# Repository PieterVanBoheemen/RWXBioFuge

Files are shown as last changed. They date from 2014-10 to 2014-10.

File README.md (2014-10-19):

RWXBioFuge
==========

Centrifugation is a powerful method for isolation of compounds such as DNA, proteins, oil or membrane vesicles from a complex mixture. The RWXBioFuge was designed to bring this powerful tool into the hands of labtechnicans, scientists, hackers, makers, diybio-ers and those who cannot afford to procure A-label equipment in low-resource settings. 

It may also be used as an educational project to teach some fundamental principles of physics, chemistry, biology and electronics hands-on. Apart from an assembly guide, this documentation also includes [7 instructions for demonstration experiments and science classes][6].

For assembly workshops or any questions, remarks or suggestions please contact pietervanboheemen@gmail.com

This repository contains the code, source files and instructions for operating the RWXBioFuge Open Source microcentrifuge.

- [ArduinoCode][1]: source code for the Arduino Ethernet
- [Rotor][2]: OpenSCAD source code for the rotor, preview at [YouMagine][5]
- [Device][3]: Bill of Materials, 3D model, 2D CAD files and Fritzing wiring
- [Docs][4]: assembly and tutorial documents

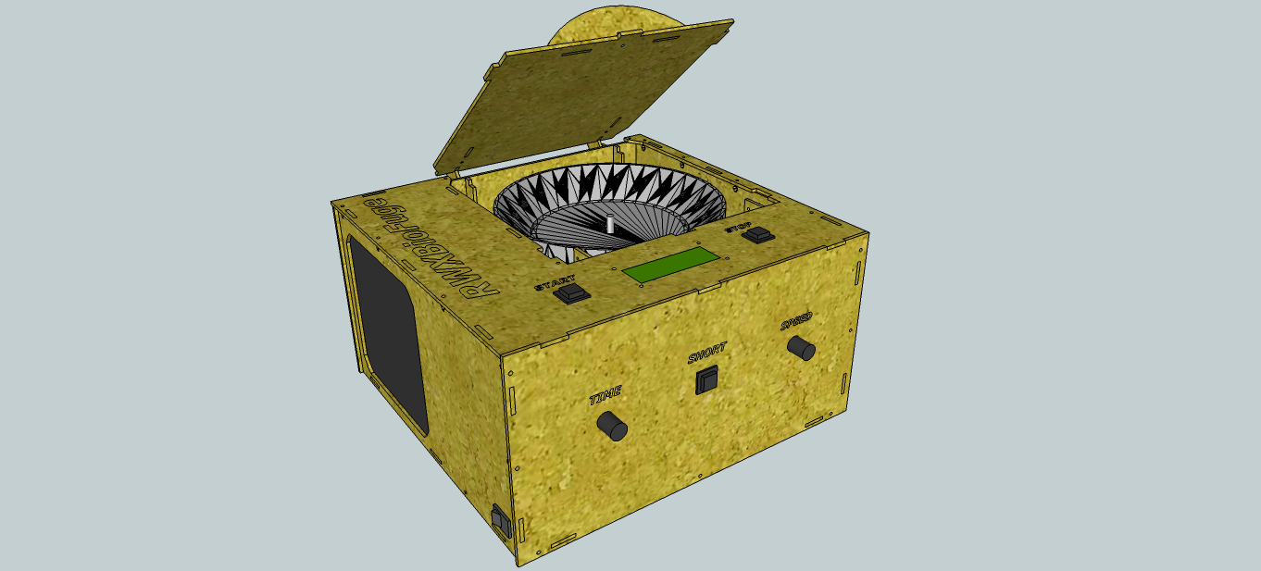
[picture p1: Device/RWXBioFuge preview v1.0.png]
Render

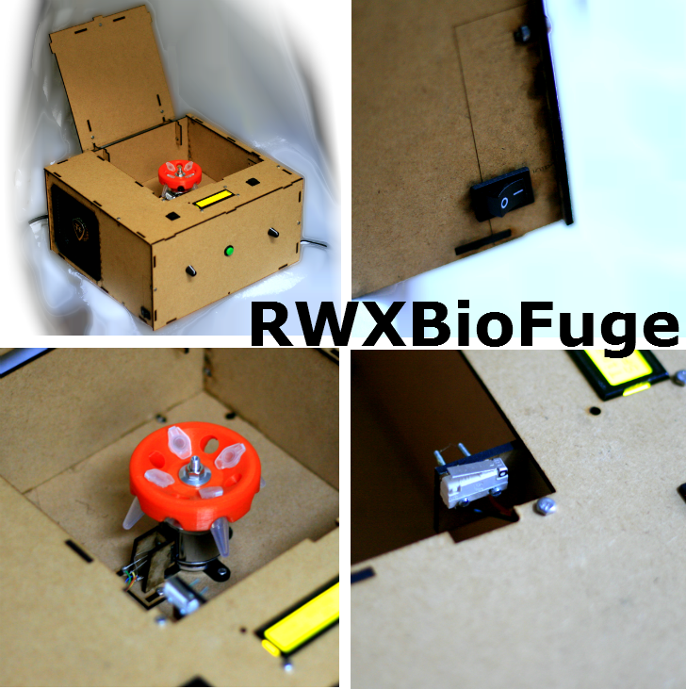
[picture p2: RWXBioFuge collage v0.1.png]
Pictures

Beneden Leeuwen

The V0.1 machine is used in the [Waag Society's Open Wetlab][10] and future improvements will be made during the [Open Wetlab open evenings][11].

> **WARNING**: Fast spinning rotors are dangerous! Make sure you read the [safety instructions][7] before use.

> **LICENSE**: All work in this project is licensed under the [Creative Commons Attribution-ShareAlike 4.0 International License][8]. In other words: you are free to use everything in this repository as long as you attribute Pieter van Boheemen and share derivative work under the same conditions.

###Release notes and features of V1.0
The V1.0 release of the RWXBioFuge contains the following features:
- Completely Open Source and designed in freely available software, such as Arduino IDE, Sketchup, OpenSCAD, InkScape and Fritzing 
- Constructed out of solely off-the-shelf or digitally fabricated parts
- High speed centrifuge > 10,000 RPM, depending on your own settings and confidence
- Configurable speed in percentages of full power
- Configurable time in convenient steps, including infinite
- Separate Start and Stop buttons
- Current RPM, Gforce and remaining time is displayed during operation
- A button for Short immediate operation
- Open lid detector
- Web interface to set, start and stop the machine, including status during operation

###Release notes of V0.1
V0.1 is the first development release of RWXBioFuge. It is still in experimental phase with plenty of bugs. All V0.1 source files will be replaced when V1.0 is ready.

###To Do
The following upgrades are planned for the next version:
- Step by step graphical assembly guide in Instructables style
- Optimization of Power Supply, ESC and motor setup to save costs
- Reduced size of the casing by better placement of components
- Single rotary encoder interface to save costs
- Magnetic lid lock to increase safety
- Accelerometer for the detection of unbalanced rotor through vibrations to increase safety
- Transparent window in lid
- Numbered tube holes in rotor
- Different types of rotors, for various number and sizes of tubes and Hct
- Improved graphical Web User Interface 

Credits: This project has been greatly inspired by the work, advise and help of:

    DIYBio Groningen for printing the first rotor at Beneden-Leeuwen Mini Maker Faire
	Cathal Garvey - Dremelfuge
    Karlin Yeh - OpenFuge
    Drevious - Microfuge 8 Place Rotor
    Hackteria - Hacked Hard Disk centrifuge

[1]:https://github.com/PieterVanBoheemen/RWXBioFuge/blob/master/ArduinoCode/
[2]:https://github.com/PieterVanBoheemen/RWXBioFuge/blob/master/Rotor/
[3]:https://github.com/PieterVanBoheemen/RWXBioFuge/blob/master/Device/
[4]:https://github.com/PieterVanBoheemen/RWXBioFuge/blob/master/Docs/
[5]:https://www.youmagine.com/designs/microcentrifuge-20-place-rotor
[6]:https://github.com/PieterVanBoheemen/RWXBioFuge/blob/master/Docs/Tutorials/
[7]:https://github.com/PieterVanBoheemen/RWXBioFuge/blob/master/Docs/Usage/
[8]:http://creativecommons.org/licenses/by-sa/4.0/
[9]:http://www.diybiogroningen.org/mini-mini-maker-faire-in-beneden-leeuwen/
[10]:http://waag.org/en/lab/open-wetlab
[11]:http://www.meetup.com/Dutch-DIY-Bio/

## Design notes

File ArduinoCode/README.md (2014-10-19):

RWXBioFuge Arduino Code
=======================

Input:
- Time rotary encoder
- RPM rotary encoder
- Start button
- Short run button
- Lid detector
- Infrared RPM sensor
- Ethernet

Output:
- Pulses for Electronic Speed Controller
- Serial USB
- Ethernet
- I2C 16x2 LCD display

Dependencies:
- Webduino https://github.com/sirleech/Webduino
- AdaEncoder https://code.google.com/p/adaencoder/
- ooPinChangeInt https://code.google.com/p/oopinchangeint/
- LiquidCrystal_I2 http://hmario.home.xs4all.nl/arduino/LiquidCrystal_I2C/

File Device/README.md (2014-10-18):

Device
======

The RWXBioFuge consists of solely of-the-shelf parts and laser cut wood that has been designed in Sketchup. Using these source files and the [Assembly Guide][1], you can build your own.

In this folder you will find:

- The Bill of Materials (BoM)
- 3D SketchUp design file
- 2D SVG files of each part
- Fritzing wiring of Breadboard or Shield

[1]: https://github.com/PieterVanBoheemen/RWXBioFuge/blob/master/Docs/Assembly/

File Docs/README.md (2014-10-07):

RWXBioFuge documentation
=======================

This folder contains the documentation of the RWXBioFuge project, including an assembly guide, usage instructions and tutorial experiments. 

----------

#### Assembly Guide
Information on how to assemble the RWXBioFuge. [Read Assembly Guide][1]
#### Tutorial Experiments
Fun experiments to start exploring the usage of the RWXBioFuge. [Read Tutorial Experiments][2]
#### Usage Instructions
Basic instructions on how to use the RWXBioFuge. [Read Usage Instructions][3]

[1]:https://github.com/PieterVanBoheemen/RWXBioFuge/blob/master/Docs/Assembly/
[2]:https://github.com/PieterVanBoheemen/RWXBioFuge/blob/master/Docs/Tutorials/
[3]:https://github.com/PieterVanBoheemen/RWXBioFuge/blob/master/Docs/Usage/

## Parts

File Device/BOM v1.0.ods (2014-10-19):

The links offered in this BoM are mere suggestions. Have a look on eBay or Alibaba to find cheaper alternatives
Description | Amount | URL | Remarks
Push button | 3 | http://nl.farnell.com/apem/1415nc-black/switch-spdt-black/dp/1082275?Ntt=1082275 | APEM - 1415NC BLACK - SWITCH, SPDT, BLACK
Lid lever switch | 1 | http://nl.farnell.com/itw-switches/19n403l18/microswitch-v4-lever/dp/624676?Ntt=624676 | ITW SWITCHES - 19N403L18 - MICROSWITCH, V4, LEVER
IR RPM sensor | 1 | http://nl.farnell.com/fairchild-semiconductor/qrd1114/opto-switch-reflective/dp/1467858?Ntt=1467858 | FAIRCHILD SEMICONDUCTOR - QRD1114 - OPTO SWITCH, REFLECTIVE
16x2 LCD display with I2C module | 1 | https://iprototype.nl/products/components/led-lcd/lcd16x2-I2C-BL | These displays are also commonly found on eBay: http://www.ebay.com/itm/1602-LCD-16X2-Character-Display-IIC-I2C-TWI-SPI-I2C-Serial-Interface-Board-/371158866343?pt=LH_DefaultDomain_0
Rotor | 1 | https://www.youmagine.com/designs/microcentrifuge-20-place-rotor | Print it yourself, via Shapeways or 3Dhubs
Power Supply | 1 | http://www.thermaltake.com/products-model.aspx?id=C_00001830 | ThermalTake SMART M850W
Electronic Speed Controller | 1 | http://www.hobbyking.com/hobbyking/store/uh_viewItem.asp?idProduct=33371 | Hobbyking SS Heli Series 50-65A ESC
Brushless motor | 1 | http://www.hobbyking.com/hobbyking/store/uh_viewItem.asp?idProduct=39962 | Turnigy Aerodrive SK3 - 4240-740kv Brushless Outrunner Motor
Power switch | 1 | https://iprototype.nl/products/components/buttons-switches/rocker-switch-large | RLEIL ROCKER SWITCH
Arduino Ethernet |  |  | Buy it at your favorite Arduino dealer
Lasercut out of 3mm MDF |  |  | Cut it yourself, or via Ponoko / Formulor
2.2kOhm | 4 | http://nl.farnell.com/multicomp/mcf-0-25w-2k2/resistor-carbon-film-2k2-0-25w/dp/9339302?Ntt=9339302 | MULTICOMP - MCF 0.25W 2K2 - RESISTOR, CARBON FILM, 2K2, 0.25W, 5%
220Ohm | 1 | http://nl.farnell.com/multicomp/mcf-0-25w-220r/resistor-carbon-film-220r-0-25w/dp/9339299?Ntt=9339299 | MULTICOMP - MCF 0.25W 220R - RESISTOR, CARBON FILM, 220R, 0.25W, 5%
6.8kOhm | 1 | http://nl.farnell.com/multicomp/mcf-0-25w-6k8/resistor-carbon-film-6k8-0-25w/dp/9339663?Ntt=9339663 | MULTICOMP - MCF 0.25W 6K8 - RESISTOR, CARBON FILM, 6K8, 0.25W, 5%
Rotary encoder | 2 | https://www.sparkfun.com/products/9117 | ALPHA 318-ENC130175F-12PS
Knob | 2 | http://nl.farnell.com/multicomp/cr-r4-7/knob-soft-touch-d-shaft-black/dp/1440012?Ntt=1440012 | MULTICOMP - CR-R4-7 - KNOB, SOFT TOUCH, D SHAFT, BLACK
3.5 mm connectors | 1 | http://www.hobbyking.com/hobbyking/store/__20228__Individual_HXT_3_5mm_connector_for_motor_ESC_12pc_.html | Individual HXT 3.5mm connector for motor/ESC
Protoshield | 1 | http://nl.farnell.com/arduino/a000082/prototype-shield-for-arduino-board/dp/2075379?Ntt=2075379 | ARDUINO - A000082 - PROTOTYPE SHIELD, FOR ARDUINO BOARD
Molex extension | 1 | https://www.sparkfun.com/products/11298 | 4 Pin Molex Connector – Pigtail
Stackable headers | 1 | http://www.antratek.nl/arduino-stackable-header-kit | Arduino Stackable Header Kit
M3 10 nuts and bolts | 1 | http://www.bevestigingsmateriaal.nl//index.php?productGroupId=61&productId=65210093303005 | Buy it at your local Do-It-Yourself hardware store
Generic stuff
Solder | 1
Tie wrap | 1
Wires | 20

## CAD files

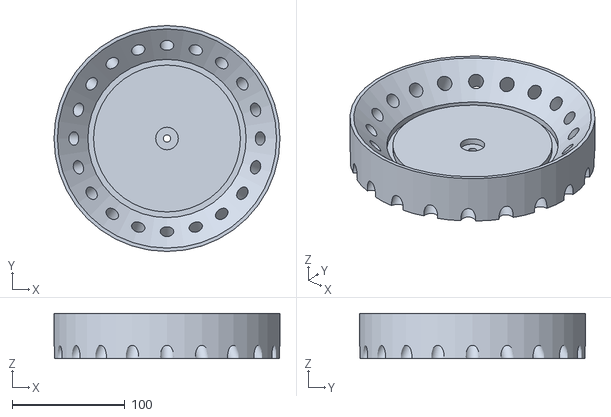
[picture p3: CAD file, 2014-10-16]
Rotor/rotor v0.1.stl
200.0 x 200.0 x 40.0

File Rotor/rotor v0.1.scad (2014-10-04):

$fn=40; // resolution of the arcs

scale([10,10,10]) { // cm to mm scaling

difference () { // substract tube holders from outer ring

difference () { // substract inner groove

	difference() { // substract cone from main disk

		translate([0,0,-0.4])
		cylinder (h = 4, r=12); // main disk

		translate([0,0,1]) // raise cone from bottom
		cylinder (h = 2.7, r1 = 8, r2 = 10.8, center = false); // cone

		translate([0,0,-0.6])
		cylinder (h = 1.6, r=0.635); // axis

		translate([0,0,0.5]) // groove around axis
		cylinder (h = 0.5, r=1);

	}

	// groove under tube holders
	translate([0,0,0.5])
	difference() { // ring
		cylinder (h = 0.5, r = 8);
		cylinder (h = 0.5, r = 7.5);
	}

}

//tube holding cylinders
translate([-11.5,0,-1]) rotate([0,35,0]) cylinder(h=8, r=1.2);
translate([11.5,0,-1]) rotate([0,-35,0]) cylinder(h=8, r=1.2);

translate([0,-11.5,-1]) rotate([0,35,90]) cylinder(h=8, r=1.2);
translate([0,11.5,-1]) rotate([0,-35,90]) cylinder(h=8, r=1.2);

translate([-11.5 * cos(22.5), -11.5 * sin(22.5),-1]) rotate ([0,35,22.5]) cylinder(h=8, r=1.2);
translate([-11.5 * cos(45),-11.5 * sin(45),-1]) rotate ([0,35,45]) cylinder(h=8, r=1.2);
translate([-11.5 * cos(67.5),-11.5 * sin(67.5),-1]) rotate ([0,35,67.5]) cylinder(h=8, r=1.2);

translate([-11.5 * cos(22.5), 11.5 * sin(22.5),-1]) rotate([0,35,-22.5]) cylinder(h=8, r=1.2);
translate([-11.5 * cos(45), 11.5 * sin(45),-1]) rotate([0,35,-45]) cylinder(h=8, r=1.2);
translate([-11.5 * cos(67.5), 11.5 * sin(67.5),-1]) rotate([0,35,-67.5]) cylinder(h=8, r=1.2);

translate([11.5 * cos(22.5), -11.5 * sin(22.5),-1]) rotate([0,-35,-22.5]) cylinder(h=8, r=1.2);
translate([11.5 * cos(45), -11.5 * sin(45),-1]) rotate([0,-35,-45]) cylinder(h=8, r=1.2);
translate([11.5 * cos(67.5), -11.5 * sin(67.5),-1]) rotate([0,-35,-67.5]) cylinder(h=8, r=1.2);

translate([11.5 * cos(22.5), 11.5 * sin(22.5),-1]) rotate([0,-35,22.5]) cylinder(h=8, r=1.2);
translate([11.5 * cos(45), 11.5 * sin(45),-1]) rotate([0,-35,45]) cylinder(h=8, r=1.2);
translate([11.5 * cos(67.5), 11.5 * sin(67.5),-1]) rotate([0,-35,67.5]) cylinder(h=8, r=1.2);
}

}

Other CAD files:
Device/RWXBioFuge v1.0.skp

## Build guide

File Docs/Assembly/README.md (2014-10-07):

Assembly Guide
==============

Hi fellow DIY Centrifugator,

Welcome to the RWXBioFuge assembly guide! By following these step by step instructions you will have your RWXBioFuge spinning within 2 hours. Finally the force of centrifugation on your DIY lab bench at your disposal.

Whenever you feel like something is unclear, use the commenting section here on GitHub to post your remarks.

The assembly guide consists of four steps:

- [00 Getting Started][0]
- [01 Casing][1]
- [02 Wiring][2]
- [03 Programming][3]
- [04 Final][4]

[0]: https://github.com/PieterVanBoheemen/RWXBioFuge/blob/master/Docs/Assembly/00-Getting-Started.md
[1]: https://github.com/PieterVanBoheemen/RWXBioFuge/blob/master/Docs/Assembly/01-Casing.md
[2]: https://github.com/PieterVanBoheemen/RWXBioFuge/blob/master/Docs/Assembly/02-Wiring.md
[3]: https://github.com/PieterVanBoheemen/RWXBioFuge/blob/master/Docs/Assembly/03-Programming.md
[4]: https://github.com/PieterVanBoheemen/RWXBioFuge/blob/master/Docs/Assembly/04-Final.md

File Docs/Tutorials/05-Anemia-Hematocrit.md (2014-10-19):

05 Anemia diagnosis and hematocrit measurement
==============================================

> **WARNING**: Blood may carry diseases such as HIV and Hepatitis B. Wear protective gloves when handling other peoples blood and clean everything thoroughly. DIY experiments should never be interpreted as a medical diagnosis, go see a doctor instead.

Hematocrit values are measured to determine whether blood has a sufficient number of erythrocytes. These are necessary to transfer oxygen. However, if the concentration is too high, the blood's viscosity becomes a problem.

The blood of consists of plasma, red blood cells and white blood cells. When a sample is centrifuged, the red cells sink to the bottom. The plasma will be on top and a thin layer of white cells can be found on top of the red cells pellet. The volume ratio between red cells and the total volume is the Hct value.

Normal Hct values are around 47 percent for men, and 42 percent for women. Anemia occurs when the Hct value is below 40 for men, and below 37 for women.

### Materials
- Ethanol (70%)
- Soap and water
- Gloves
- Sterile lancets
- Cotton ball
- Hematocrit tubes (for which you need a hematocrit head), or small centrifuge tubes preferably graded
- Trash container

### Procedure
- Wash your hands with soap and water
- Clean a finger you don't use that much, such as ring finger, with 70% ethanol
- Pierce the fingertip with a quick prick to the side
- The first liquid is hardly any blood, so wipe it off with the clean and dry cotton ball
- By squeezing your fingertip blood will drip into the hematocrit or centrifuge tube
- Balance a second tube with the same weight and place on opposite sides of the centrifuge
- Spin at full speed for 5 minutes
- Determine the percentage of red blood cells

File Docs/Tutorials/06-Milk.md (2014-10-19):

06 Break down whole milk into cream and skim milk
=================================================

Whole milk consist for about 4% of fat. Centrifuges can be used to separate the cream from the skim milk.

### Materials
- 2 mL centrifuge tubes (for bigger volumes you need a different rotor)
- Whole milk
- Transfer pipettes
- Stove
- Thermometer

### Procedure
- Warm up the whole milk to about 40 degrees Celcius
- Transfer the whole milk into centrifuge tubes. Make sure they're balanced.
- Spin at maximum speed for 5 minutes
- Observe the separation
- Try to pipette the skim milk into fresh tubes

### Additional steps
You may continue to analyse the resulting cream and skim milk with a density meter or even a microscope.

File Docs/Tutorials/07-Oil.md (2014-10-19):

07 Oil and water separation
===========================

In this experiment we will investigate the influence of detergents on the ability of the centrifuge to seperate water and oil.

### Materials
- Oil, such as olive oil, sunflower oil or palm oil
- Water from the tap
- Centrifuge tubes
- Detergent, such as hand soap or dishwashing soap 

### Procedure
- Prepare a dilution series of oil in water
- Add different concentrations of detergent to the mixture
- Make sure the tubes are balanced
- Spin in the centrifuge at max speed for 5 minutes
- Observe the separation profiles

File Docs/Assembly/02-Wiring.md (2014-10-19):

02 Wiring
=========

The second step is to wire all the components. Take a close look at the [Fritzing arduino shield wiring schematic][1] before connecting all the components.

1. Prepare molex connector
2. Connect brushless motor to molex connector and ATX power supply
3. Connect power switch to ATX power supply
4. Connect Electronic Speed Controller to brushless motor
5. Wire everything to the arduino shield, overlayed with the "RWXBioFuge Shield port indicator"
  1. Connect Electronic Speed Controller
  2. Connect Infra-red RPM sensor 
  3. Connect Lid lever switch
  4. Connect Electromagnet
  5. Connect the Start push button
  6. Connect the Stop push button
  7. Connect the Short push button
  6. Connect the Time rotary encoder
  7. Connect the Speed rotary encoder
  7. Connect I2C LCD
  8. Connect power supply 

> **Tip:** Use tie wraps to bundle the wires.

Continue to the following step [03 Programming][0].

[0]:https://github.com/PieterVanBoheemen/RWXBioFuge/blob/master/Docs/Assembly/03-Programming.md
[1]:https://github.com/PieterVanBoheemen/RWXBioFuge/blob/master/Device/Shield%20v1.0.fzz

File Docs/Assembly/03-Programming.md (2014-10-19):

03 Programming
==============

The third step is to preparing the Arduino Ethernet.

1. Download the latest RWXBioFuge source code and libraries from [Github][1].
2. Connect the USB to serial programming board to the Arduino Ethernet and put the USB cable in your computer.
3. Load the RWXBioFuge source code in the Arduino IDE.
4. Click on Upload to compile and transfer the code to the Arduino Ethernet.
5. Disconnect the USB to serial programming board from the Arduino Ethernet.
6. Assemble the RWXBioFuge proto shield on to the Arduino Ethernet.
7. Power up the RWXBioFuge and check whether the LCD starts by showing "RWXBioFuge" and continues to the settings menu.

Almost done, just one more step left: [04 Final][2].

[1]:https://github.com/PieterVanBoheemen/RWXBioFuge/blob/master/ArduinoCode/
[2]:https://github.com/PieterVanBoheemen/RWXBioFuge/blob/master/Docs/Assembly/04-Final.md

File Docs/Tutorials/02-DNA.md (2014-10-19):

02 DNA Extraction
=================

This procedure will teach you how to isolate DNA from biological samples like saliva. Basically what we will do is open up the cells with soap, deteriate proteins with salt and precipitate the DNA with alcohol. Using the centrifuge, the DNA will stick to the bottom of our tube for us to get rid of the rest.

### Materials
- Dish soap, hand soap or shampoo
- 10% Salt solution
- Alcohol, 95% like Spiritus is great, otherwise Vodka will also work
- Small glass
- 2 mL centrifuge tubes
- Mixing rod

### Equipment
- Centrifuge

### Procedure

- Collect a few spits of saliva in a small beaker glass
- Add a few drops of soap and mix a little with the rod
- Transfer 1 mL the mixture into a 2 mL centrifuge tube
- Add 1 mL of 10% salt solution and mix again
- Centrifuge the tube at 10.000 rpm for 5 minutes
- Transfer two times 1 mL of the supernatant into two fresh centrifuge tube
- Add 1 mL of ice cold ethanol to each tube
- Centrifuge the tubes at 10.000 rpm for 10 minutes
- Dispose of the supernatant, the pellet contains your DNA

You may wash the pellet a few times if you like by repeating the procedure.

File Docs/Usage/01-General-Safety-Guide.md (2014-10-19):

01 General Safety Guide
=======================

A microcentrifuge like the RWXBioFuge is a machine that is used in a lab to seperate matter based on the difference in weight.

For example when seperating liquids from solids, the liquid solution on top of the solids after centrifugation is called the "supernatant". The solids at the bottom of the tube the "pellet".

A typical microcentrifuge has a maximum speed of about 13,000 to 14,000 rpm (revolutions per minute). The RWXBioFuge may go much faster, but it's up to you whether you choose too.

Take the following guidelines into account when using 1.5 or 2 mL microcentrifuge tubes:

- Read the [Machine Operations manual][1] thoroughly, and make sure you understand how to start and stop the machine.

- Before powering the machine up, check whether the rotor is strongly fixed to the brushless motor.

- Stress test your assembly before using it or providing it to others. Simply fill up all 20 slots with tubes containing 2 mL of water and spin at the highest speed for 30 minutes. It is wise to put the machine in a seperate room and operate it via the [Web Interface][2] for your own safety.

- Don't start on your own. Ask for help from someone who has used a microcentrifuge before to explain the machine to you and supervise the first time you use it.
 
- Make sure the rotor and centrifuge tubes are clean and intact before use.

- **Always** balance the microcentrifuge tubes to make sure all contain the same mass, or use two tubes with the exact same amount of sample. If you need to spin only one tube, fill up a second with the same mass.

- Place the balanced tubes at the exact opposite position of eachother in the rotor.

- When using 0.5 ml or smaller microcentrifuge (PCR) tubes, put them inside of a 1.5 ml tube.

- Whenever the machine starts vibrating heavily or shaking, press the Stop button immediately.

- Whenever the machine makes unusual sounds, press the Stop button and inspect the rotor.

[1]:https://github.com/PieterVanBoheemen/RWXBioFuge/blob/master/Docs/02-Machine-Operations.md
[2]:https://github.com/PieterVanBoheemen/RWXBioFuge/blob/master/Docs/03-Web-Interface.md

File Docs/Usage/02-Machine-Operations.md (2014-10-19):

02 Machine Operations
=====================

The RWXBioFuge is not a difficult machine to operate. Still, it's wise to familiarize yourself with the user interface before conducting any experiments.

The user interface consists of:
- Power Switch
- 3 buttons
  - Start
  - Stop
  - Short
- 2 knobs
  - Time
  - Speed

### Normal user flow:
1. Start the machine by flipping the power switch, the machine will start up in Configuration Mode
2. Load the balanced samples into the rotor and close the lid
3. Turn the Time and Speed knob to set the desired length of time and percentage of power
4. Press the Start button
  - The LCD screen will show a count down and indicate then the spin is done
  - You may press the Stop button at any time to interrupt the current process
5. The machine returns to the start screen Configuration Mode
6. If you do not plan to use the machine any more, switch it off using the power switch

Flow diagram:
```flow
st=>start: Begin
io1=>inputoutput: Set Speed
io2=>inputoutput: Set Time
op1=>operation: Press Start
op2=>operation: Spin Rotor
cond=>condition: Stop Pressed
e=>end

st->io1->io2->op1->op2->cond
cond(no)->e
cond(yes)->op2
```

### "Short" user flow:
1. Start the machine by flipping the power switch, the machine will start up in Configuration Mode.
2. Load the balanced samples into the rotor and close the lid.
3. Press the Short button.
4. The rotor will start spinning immediately.
5. Release the Short button to stop the rotor.
6. The machine returns to the start screen Configuration Mode
7. If you do not plan to use the machine any more, switch it off using the power switch

Flow diagram:
```flow
st=>start: Begin
op1=>operation: Press Short
op2=>operation: Spin Rotor
cond=>condition: Short released
e=>end

st->op1->op2->cond
cond(no)->op2
cond(yes)->e
```

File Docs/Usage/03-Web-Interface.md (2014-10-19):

03 Web Interface
================

The main reason for the RWXBioFuge to have a webinterface is to enable you to safely hack and tweak the machine by operating it from a distance.

Put the machine in a separate room or a very strong container and use a regular UTP CAT5 cable to connect the RWXBioFuge to your local network.

By default the machine can be reached via http://192.168.1.210, you may change the IP address in the [source code][1].

1. Open up your browser and surf to http://192.168.1.210
2. The webinterface responds to simple POST or GET commands

Key  | Description | Possible Values
---- | ----------- | ---------------
1    | Speed (%)   | 0 to 100
2    | Time (sec)  | 0 to infinity
3    | Start       | 1 to start, 0 to do nothing
4    | Stop        | 1 to stop, 0 to continue

To tell the RWXBioFuge to spin at 20% for 2 minutes you need to surf to: http://192.168.1.210?1=20&2=120&3=1

3. Alternatively, you may use a form that allows you to send commands to the RWXBioFuge via the webinterface.
4. A frame refreshes every 2 seconds to inform you about the current status of the machine.
5. At the bottom of the page the parsed information is shown.

[1]:https://github.com/PieterVanBoheemen/RWXBioFuge/blob/master/ArduinoCode/

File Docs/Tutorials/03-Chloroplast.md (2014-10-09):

03 Chloroplast Isolation
========================

### Materials
- Fresh Spinach
- Cheese cloth or coffee filter
- 10 2 mL centrifuge tubes
- Pasteur transfer pipettes
- Beaker
- Ice
- 100 mL 0.5 M sucrose (17% w/v), store on Ice
- 80% acetone

### Equipment
- Chopping board and knife, scissors will also work
- Mortar or blender
- Centrifuge
- Microscope or spectrophotometer

### Procedure
1. Wash 10 grams of spinach leaves
2. Cut out the veins of the leaves
3. Grind the leaves in a mortar or blender
4. Add 5 mL of 0.5 M sucrose to the solution and mix
5. Filter the mixture through the cheese cloth or coffee filter into a beaker
6. Save 0.5 mL of the filtrate in a tube for comparison later on
7. Transfer two times 2 mL to two centrifuge tubes, make sure they're balanced
8. Centrifuge at low speed (50x - 200x g) for 3 - 10 minutes to get rid of cell debris (white pellet)
9. Transfer the supernatant to two fresh centrifuge tubes, save 0.5 mL of each tube for later examination
10. Centrifuge at high speed (1000x g) for 10 minutes to pellet the chloroplasts
11. Dispose the supernatant when you feel satisfied with the pellet, spin longer if you feel like it
12. Resuspend the pellet in 0.5 mL 80% acetone
13. Examine the samples under the microscope and/or measure the absorbance at OD650. You can count the number of Chloroplasts per mL

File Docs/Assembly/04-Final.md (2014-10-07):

04 Final steps
=============

The last steps are:

1. Attach the rotor on the brushless motor axis and fix it with the nut
2. Close the front panel

Well done! The RWXBioFuge is ready to be used. Please read the [Usage Instructions][1]

[1]: https://github.com/PieterVanBoheemen/RWXBioFuge/blob/master/Docs/README.md

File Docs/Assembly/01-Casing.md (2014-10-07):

01 Casing
========

The first step in assembly of the RWXBioFuge is to construct the casing.

1. Start with the back panel, labelled as "**1 Back Panel**"
2. Attach the "**2 Bottom Plate**", "**3 Elevated Bottom Plate**", "**4 Middle Seperator**", "**5 Front Separtor**" and sides "**6 Left Side Panel**", "**7 Right Side Panel**"
3. Insert the ATX Power Supply and use the scews to mount it to the Back Panel
4. Insert the buttons in the "**8 Top Panel**" and "**9 Front Panel**"
5. Mount the LCD screen in the Top Panel
6. Insert the power switch in the Left Side Panel
7. Assemble the lid and mount it to the Back Panel
8. Assemble the infrared RPM sensor and mount it on the Elevated Bottom Plate
9. Mount the Top Panel

Leave the front open for easy access to the electronics for the next step: [02 Wiring][1].

[1]: https://github.com/PieterVanBoheemen/RWXBioFuge/blob/master/Docs/Assembly/02-Wiring.md

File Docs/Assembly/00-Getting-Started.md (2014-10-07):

00 Getting Started
==================

Before you get to the actual assembly of the machine, we are going to make sure if you have everything sorted out to do so.

1. You'll need about two hours to complete the guide. Feel free to build in any breaks whenever you feel necessary. There's no rush.
2. Make some space on your workbench large enough to layout the components, get rid of other rubbish that you don't need.
3. Brew some coffee, open up a beer or poor yourself a glass of water.
4. You will need the following tools:
  - Flat head screw driver
  - Pliers (optional) for holding small parts like M3 bolts and wire header pins
5. Check whether you have all the parts:
  - Power Supply
  - Power Cord
  - USB Cord
  - Arduino Ethernet
  - Electronic components
  - Laser Cut panels
  - Nuts and bolts

> **Note:** Make sure you are in a place with enough light, it might be convenient to have a desk lamp or flash light at your disposal to illuminate areas of interest.

You're all set and ready to go, to step [01 Casing][1]

[1]: https://github.com/PieterVanBoheemen/RWXBioFuge/blob/master/Docs/Assembly/01-Casing.md

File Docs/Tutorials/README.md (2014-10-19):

Tutorials
=========

The following tutorials are for you to get started and get a grasp of the full potential of the centrifuge.

1. Principles of centrifugation
2. DNA extraction for PCR
3. Chloroplast isolation for microscopy
4. Microparticles in cosmetics
5. Anemia diagnosis and hematocrit measurement
6. Break down whole milk into cream and skim milk 
7. Oil and water separation

Please add your own medical, chemical or biological mad DIY isolation or microfiltration experiment!

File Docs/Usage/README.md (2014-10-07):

Usage Instructions
==================

These instructions clearify how to use the RWXBioFuge in a proper and safe way. 

> **Note:** Remember, the use of this machine will always remain at your own risk. Spinning centrifuges can be extremely dangerous. A flying rotor can easily take an eye or even kill you.

----------

#### 01 General Safety Guide
How to safely use a microcentrifuge. [Read][1]

#### 02 Machine Operations
How to operate the RWXBioFuge through its user interface. [Read][2]

#### 03 Web Interface
How to operate the RWXBioFuge through the web interface. [Read][3]

[1]: https://github.com/PieterVanBoheemen/RWXBioFuge/blob/master/Docs/Usage/01-General-Safety-Guide.md
[2]: https://github.com/PieterVanBoheemen/RWXBioFuge/blob/master/Docs/Usage/02-Machine-Operations.md
[3]: https://github.com/PieterVanBoheemen/RWXBioFuge/blob/master/Docs/Usage/03-Web-Interface.md

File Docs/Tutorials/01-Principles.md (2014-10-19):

01 Principles of Centrifugation
===============================

The goal of this first tutorial is for you to understand the basic physics behind centrifugation.

Centrifugation is a technique often used in a laboratory to separate two liquids or a liquid and a solid. It is based on the effect of gravity on these components. Under normal circumstances two components may separate just by letting the mixture rest. Heavy components will sink to the bottom due to gravity. However, in some cases the differences are too small or other forces such as hydrophobic interactions keep components together. In these situations you need centrifugation to increase the separation rate.

Note: centrifugal force is not a force in itself, but the result of inertia.

### Centrifugal force
**Centrifugal force** is mathematically described as:

F_{c}=mr w^{2}

Fc is the force acting on a particle

r is the radius

m is the mass of the particle

w is the **angular velocity of the particle**

The angular velocity can also be defined as a function of Revolutions per Minute (RPM) w=2pN/60

N is the number of revolutions per minute

So the centrifugal force is:

F_{c}=mr (2pN/60)^{2}=0.011mr N^{2}

### G force
When comparing the above equation to the gravity on a particle, you will notice the similarities:

F_(c)=mg

It can be seen that g is equal to 0.011rN^2. This is why the centrifugal force is often expressed as "g".

### Example

***Question:*** Let's spin a liquid at 2000 RPM at a radius of 10 cm, what is the amount of "g" on the particle?

***Answer:*** 

g=F_{c} \div F_{g}=(0.011r N^{2}) \div g=(0.011 \times 0.1 \times 2000^{2}) \div 9.81 = 450

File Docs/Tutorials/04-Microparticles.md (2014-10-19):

04 Microparticles in cosmetics
===============================

Microparticles and nanospheres are often applied in cosmetics. The particles can be loaded with pigments and/or add positive of negative surface charge. With the right size, the particles have a ball-bearing effect in creams and lotions to give it a silky texture. In scrubs the particles are added to help remove dead cells from the skin.

In this experiment we will investigate the microparticle content of every day cosmetics.

You will need the following.

Cosmetic products, such as:
- Creams
- Lotions
- Cleansers
- Scrubs
- Powder and/or liquid concealers

Dilution agents, such as:
- Water
- Ethanol
- Acetone
- Glycerine

Procedure:
- Make dilution series of the products, for example 1:1, 1:10, 1:100 and 1:1000
- Spin at maximum speed in the centrifuge for 5 minutes
- Report the amount of pelleted particles

By changing the power of the centrifuge you will get an indication of the size of the particles. The lower the speed, the havier / bigger the particles.

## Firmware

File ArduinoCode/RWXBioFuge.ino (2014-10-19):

/*
@ RWXBioFuge
@ Version: 1.0
@ Author: Pieter van Boheemen 
@ Email: pietervanboheemen@gmail.com
@ Repository: github.com/PieterVanBoheemen/RWXBioFuge

! Note:
Tested third party libraries are available through the RWXBioFuge repository. Please go to the original repositories to find the latest versions whenever needed.

The code is a bit heavy on libraries, because both the ESC and two Rotary encoders need interrupts
*/

#include <Wire.h>
#include <SPI.h>
#include <Ethernet.h> // Webserver
#include "avr/pgmspace.h"
#include "RWXBioFuge.h"
#include <Servo.h> // Electronic Speed Controller
#include "WebServer.h" // Webserver
#include <ByteBuffer.h> // Rotary encoder
#include <ooPinChangeInt.h> // Rotary encoder
#include <AdaEncoder.h> // Rotary encoder

/* *******************************************************
/  Rotary Encoder
*/
#define ENCA_a 8
#define ENCA_b 9
#define ENCB_a A0
#define ENCB_b A1
AdaEncoder encoderA = AdaEncoder('a', ENCA_a, ENCA_b);
AdaEncoder encoderB = AdaEncoder('b', ENCB_a, ENCB_b);
int8_t clicks=0;
char id=0;
int time_counter = 0;
int rpm_counter = 0;
/* ******************************************************* */

/* *******************************************************
/  LCD
*/
// Set the LCD address to 0x27 for a 16 chars and 2 line display
LiquidCrystal_I2C lcd(0x27,16,2);
/* *******************************************************
*/

/* *******************************************************
/  Global Machine Settings
*/
static int Settings[2] = { 0, 0}; // RPM goal, time
/* *******************************************************
*/

/* *******************************************************
/  Machine User Interface Buttons
*/
boolean Locked = false; // Lid lock
boolean Short = false; // Short spin button
boolean Start = false; // Start button
boolean Stop = false; // Stop button
/* *******************************************************
*/

/* *******************************************************
/  Time tracking variables
*/
uint32_t lastTick = 0; // Global Clock
uint32_t stateStartTime = 0; // Start state Clock
uint32_t StateDt; // Time within a state
uint32_t PhaseStartTime = 0;
int LCDTime = 0;
/* *******************************************************
*/

/* *******************************************************
/  RPM calculations
*/
int CurrentRPM = 0; // Current average RPM
int PrevRPM = 0; // Previous RPM
double RPMtime = 0; // RPM time
double RPMnow = 0; // Measured RPM
double Gforce = 0; // Calculated GForce
int InfraPin = 2; // Infrared sensor pin
/* *******************************************************
*/

/* *******************************************************
/  Set the initial state of the machine
*/
const char* state = "StateProgramming";
/* *******************************************************
*/

/* *******************************************************
/  Define Electronic Speed Control
*/
Servo esc;
/* *******************************************************
*/

/* *******************************************************
/  Panic switch for emergency break
*/
boolean breakopp = false;
/* *******************************************************
*/

/* *******************************************************
/  Network configuration.
*/
//  Mac Address 
static uint8_t mac[] = { 0x90, 0xA2, 0xDA, 0x0D, 0xDE, 0xDE };
// IP Address
static uint8_t ip[] = { 192, 168, 1, 210 };
// ROM-based messages used by the application, saves RAM
P(Page_start) = "<html><head><title>RWXBioFuge</title></head><body><h1>RWXBioFuge Webcontrol</h1><hr /><h2>Commands</h2><table><tbody><tr><th>1 = Time</th><td>set length of centrifugation</td></tr><tr><th>2 = RPM</th><td>Speed in %</td></tr><tr><th>3 = Start</th><td>1 to start</td></tr><tr><th>4 = Stop</th><td>1 to stop</td></tr></tbody></table><br /><hr /><h2>Send commands to RWXBioFuge</h2><form action='index.html' method='get'>Time (seconds): <input type='text' name='1' value='0' /><br />Speed (0-100%): <input type='text' name='2' value='0' /><br /><button name='3' type='submit' value='1'>Start</button> <button name='4' type='submit' value='1'>Stop</button></form><hr /><iframe src='status.html' height='180'></iframe><hr /> \n";
P(Status_start) = "<html><head><meta http-equiv='refresh' content='2'></head><body><h2>Status</h2><table><tbody><tr><td>Set Time</td><td>";
P(Status_2) = "</td></tr><tr><td>Set Speed</td><td>";
P(Status_3) = "</td></tr><tr><td>Current Speed</td><td>";
P(Status_4) = "</td></tr><tr><td>Time remaining</td><td>";
P(Status_5) = "</td></tr></tbody></table></body></html>";
P(Page_end) = "</body></html>";
P(Get_head) = "<h3>GET from ";
P(Post_head) = "<h3>POST to ";
P(Unknown_head) = "<h3>UNKNOWN request for ";
P(Default_head) = "unidentified URL requested.</h3>\n";
P(Parsed_head) = "index.html requested.</h3>\n";
P(Good_tail_begin) = "Commands received via URL tail = '";
P(Bad_tail_begin) = "INCOMPLETE URL tail = '";
P(Tail_end) = "'<br>\n";
P(Parsed_tail_begin) = "Parameters:<br>\n";
P(Parsed_item_separator) = " = '";
P(Params_end) = "End of parameters<br>\n";
P(Post_params_begin) = "Parameters sent by POST:<br>\n";
P(Line_break) = "<br>\n";
// This creates an instance of the webserver.  By specifying a prefix
// of "", all pages will be at the root of the server. 
#define PREFIX ""
WebServer webserver(PREFIX, 80);
#define NAMELEN 2
#define VALUELEN 32
#define WEBDUINO_FAIL_MESSAGE "<h1>Request Failed</h1>"
int webstart = 0;
int webstop = 0;

void parsedCmd(WebServer &server, WebServer::ConnectionType type, char *url_tail, bool tail_complete)
{
  URLPARAM_RESULT rc;
  char name[NAMELEN];
  char value[VALUELEN];

  // this line sends the standard "we're all OK" headers back to the
  // browser
  server.httpSuccess();

  // if we're handling a GET or POST, we can output our data here.
  // For a HEAD request, we just stop after outputting headers. */
  if (type == WebServer::HEAD)
    return;

  server.printP(Page_start);
 
  switch (type)
    {
    case WebServer::GET:
        server.printP(Get_head);
        break;
    case WebServer::POST:
        server.printP(Post_head);
        break;
    default:
        server.printP(Unknown_head);
    }

    server.printP(Parsed_head);
    server.printP(tail_complete ? Good_tail_begin : Bad_tail_begin);
    server.print(url_tail);
    server.printP(Tail_end);

  if (strlen(url_tail))
    {
    server.printP(Parsed_tail_begin);
    while (strlen(url_tail))
      {
      rc = server.nextURLparam(&url_tail, name, NAMELEN, value, VALUELEN);
      if (rc == URLPARAM_EOS)
        server.printP(Params_end);
       else
        {
        parseVars(server, name, value);

        storeValue(name, value); 
        }
      }
    }
  if (type == WebServer::POST)
  {
    server.printP(Post_params_begin);
    while (server.readPOSTparam(name, NAMELEN, value, VALUELEN))
    {
      parseVars(server, name, value);

      storeValue(name, value); 
    }
  }
    
  server.printP(Page_end);

}

void storeValue(char name[32], char value[32]) {
      if(atoi(name) == 1) Settings[1] = atoi(value);
      if(atoi(name) == 2) Settings[0] = atoi(value);
      if(atoi(name) == 3) webstart = atoi(value); 
      if(atoi(name) == 4) webstop = atoi(value); 
}

void parseVars(WebServer &server, char name[32], char value[32]) {
      if(atoi(name) == 1) { server.print(F("Time")); }
      else if(atoi(name) == 2){ server.print(F("RPM")); }
      else if(atoi(name) == 3){ server.print(F("Start")); }
      else if(atoi(name) == 4){ server.print(F("Stop")); }
      else { server.print(name); }
      server.printP(Parsed_item_separator);
      server.print(value);
      server.printP(Tail_end); 
}

void statusCmd(WebServer &server, WebServer::ConnectionType type, char *url_tail, bool tail_complete)
{
  server.printP(Status_start);
  server.print(Settings[1]);
  server.printP(Status_2);
  server.print(Settings[0]);
  server.printP(Status_3); 
  server.print(CurrentRPM);
  server.printP(Status_4); 
  if(state != "StateProgramming" && state != "StatePanic" && state != "StateUnlock") {
    server.print(time(Settings[1] - StateDt/1000));
  }
  else {
    server.print(0);
  }
  server.printP(Status_5); 
}

void my_failCmd(WebServer &server, WebServer::ConnectionType type, char *url_tail, bool tail_complete)
{
  // this line sends the "HTTP 400 - Bad Request" headers back to the
  //   browser
  server.httpFail();

  // if we're handling a GET or POST, we can output our data here.
  // For a HEAD request, we just stop after outputting headers. */
  if (type == WebServer::HEAD)
    return;

  server.printP(Page_start); 
  server.printP(Page_end);

}
/* *******************************************************
*/

void setup() {
      	// Update clock
	lastTick = millis();

	// Initialize I2C
	Wire.begin();

	// Open serial connection
	Serial.begin(9600);
        Serial.println(F("RWXBioFuge Started"));

	// Initialize the LCD
	lcd.init();
	lcd.backlight();
	lcd.clear();
	lcd.setCursor(0,0);
	lcd.print(F("RWXBioFuge"));
        delay(1000);
        lcd.clear();

	// Initialize buttons
	pinMode(3, INPUT); // Start button
	pinMode(4, INPUT); // Short button
	pinMode(5, INPUT); // Limit switch of the lid
        pinMode(6, INPUT); // Stop button
       
        // initialize the Ethernet adapter
        Ethernet.begin(mac, ip);
        /* setup our default command that will be run when the user accesses
         * the root page on the server */
        webserver.setDefaultCommand(&parsedCmd);
        /* setup our default command that will be run when the user accesses
         * a page NOT on the server */
        webserver.setFailureCommand(&my_failCmd);
        /* run the same command if you try to load /index.html, a common
         * default page name */
        webserver.addCommand("index.html", &parsedCmd);
        webserver.addCommand("status.html", &statusCmd);
        /* start the webserver */
        webserver.begin();
        
        // Initialize ESC control
        esc.attach(7);

}
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

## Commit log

2014-01-04 Initial arduino code
2014-10-04 Update RWXBioFuge.ino
    internet interface, better checks on lid sensor, rotary encoder instead of potmeter
2014-10-04 Create rotor.scad
    First version of 16 tube rotor
    [rotor.scad]
2014-10-07 Update and rename README.md to ArduinoCode/README.md
2014-10-16 Device files 0.1
    [BOM v0.1.ods, RWXBioFuge.skp, Rotor.scad, Rotor.stl]
2014-10-16 Relocate Rotor
    [Rotor.scad, Rotor.stl]
2014-10-18 Fritzing wiring
    [Breadboard v1.fzz, Shield v1.fzz]
2014-10-18 assembled machine
2014-10-19 Release V1.0
    [BOM v0.1.ods, BOM v1.0.ods, Breadboard v1.fzz, RWXBioFuge v1.0.skp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]
